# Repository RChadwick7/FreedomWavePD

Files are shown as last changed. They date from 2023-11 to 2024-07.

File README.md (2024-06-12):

# FreedomWavePD
### An open source version of the equipment used by researchers to treat Parkinson's Disease.
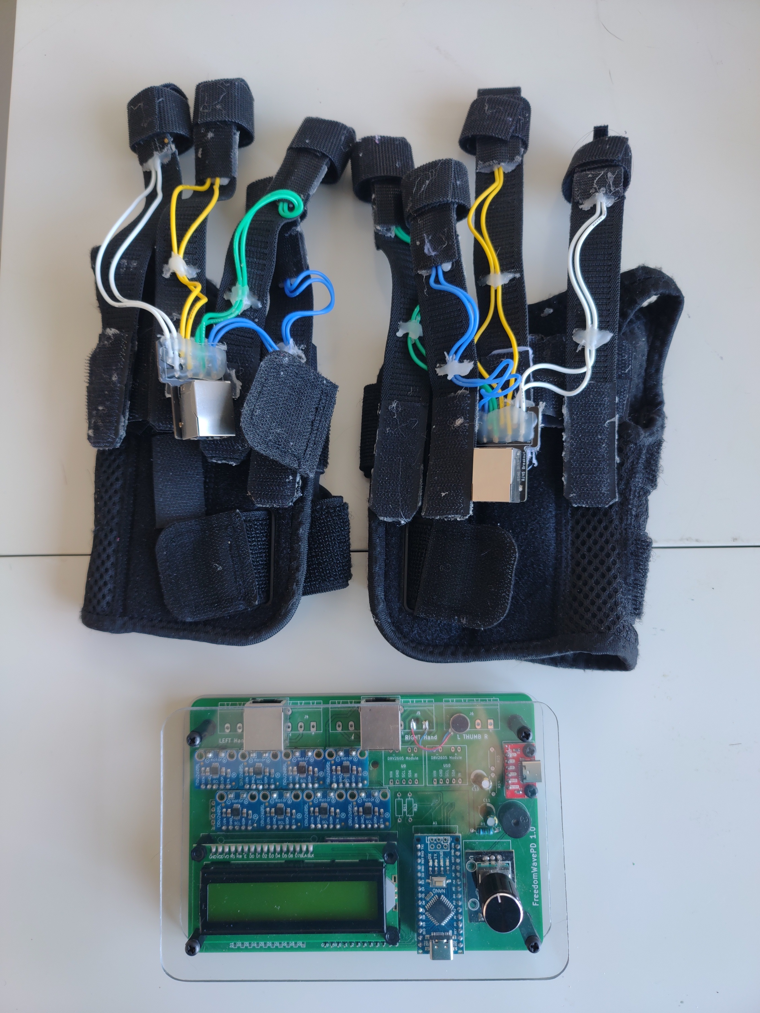
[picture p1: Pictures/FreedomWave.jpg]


- UPDATE 05-18-2024 The menu is now implemented in the firmware.
- UPDATE 02-19-2024 The PCB file should now be good. You can now see the assembly video here: https://youtu.be/leJTp28FIpU . The PCB used in the video had a few small mistakes that were corrected in the posted PCB and Gerbers, as well as the links to ordering a PCB.

**** If you don't know what this is, see this video: https://youtu.be/YEEwbxFT4Bc?feature=shared

Like many others, one morning I was watching the news and saw a story about Dr. Peter Tass at Stanford who was using vibrating gloves to treat Parkinson's Disease with amazing results. Realizing it might be years before they become available, I decided to make my own. What should have been a month of work stretched out to 8 months as I have very limited spare time. 

The theory of these gloves is relatively simple. You attach a device that either vibrates or physically pushes a small pin into the skin (NOT breaking the skin) to each finger, minus the thumbs (8 in total). These are activated in specific random patterns. The vibration triggers nerves in the fingers and these nerves go up to the brain. When these nerves are triggered in certain patterns, they can, in simple terms, help the brain straighten itself out. Look at Dr. Tass's work for much more detail.

The design goals were to make everything as flexible and adjustable as possible. While the results seem incredible, the researchers don't necessarily know the best settings yet. The gloves I constructed are bulky and awkward to put on but have the advantage of being able to put the vibrator anywhere on the fingertip. The circuit uses 8 DRV2605L haptic driver ic's but has room for 10 DRV2605L's in case there may be a benefit to using the thumbs. While these are more expensive than simple transistor drivers, they will easily drive both ERM and LRA vibrators. If there's demand, I'll design a daughterboard that will let this drive Piezo actuators.

Another design goal was to make this as easy as possible to make. I originally had hoped this could be done without soldering, but this just doesn't seem likely. My intention is that you will be able to order a PCB and all components, solder mostly modules to the PCB, and make the gloves. I have a video on YouTube showing step by step how to make the control box.

What are ERM and LRA motors? ERM stands for Eccentric Rotating Mass. Basically, they are motors that spin, and have an unbalanced weight on the output. When you add electricity, the motors spin, and they vibrate. LRA work a little differently. Linear Resonant Actuators have a magnet on a spring and a coil. If you have seen how loudspeakers work, these work on a very similar principle. When you add voltage, the coil generates a magnetic field and either repulses or attracts the magnet. If you reverse the polarity, the magnet is either attracted or repulsed, based on the polarity. If you keep alternating the polarity, the magnet will keep moving back and forth. While you can alternate the current at any frequency you want, these tend to resonate at specific frequencies and work best when you drive them at their resonant frequency.

The current state of the project is that everything should be functional. It implements all the patterns properly (I spent a LOT of time making sure randomness and jitter were spot on). The menu allows you to configure the control box to work with your specific gloves (ERM, LRA, Other) as well as treatment time, jitter, hand mirror, and others. More polish and features will be added as needed but everything is functional.

The project is divided into two parts: the gloves themselves, and the controller that runs and controls the gloves. While I don't currently have directions for making them, there are pictures here that should be enough to figure it out. You can also design your own gloves, or use some else's design. I will be mostly focusing on the controller, which is the harder and more critical part of the project. I'm currently looking into using audio transducers with a 3D Printed housing. Most files are already here but I will post more details as I get them.

The code is written in BASCOM BASIC, available at https://www.mcselec.com/ . It's not free but if you want to easily program microcontrollers it's worth every penny. I purchased a license over 20 years ago and I can't recommend it enough.

The schematic is in the Hardware folder. It looks complicated but it's mainly just wires. You could make this point-to-point but making a PCB is much easier. Be aware the schematic includes a lot of stuff you may not need. Two output connectors are added for the haptic actuators. You only need one. Also, I added driver IC's for thumbs. This isn't implemented. It's just there in case thumb actuators turn out to be useful in the future.

DISCLAIMER!!!!!!! I am NOT a Doctor. I don't make any claims that these gloves will do anything, including vibrate.

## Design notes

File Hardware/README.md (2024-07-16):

.<html><body>  <p>Can YOU make a FreedomWavePD? Odds are good but not everyone has the personality to complete this project. The most important qualities are a great deal of patience, the ability to work through frustration and an ability to follow directions precisely. It also doesn't hurt if you have some kind of mechanical aptitude. If you are unsure or need more confidence, I'd recommend picking one or two kits to assemble. A list is provided of recommended kits with the prices ranging from a few dollars up to around $12.</p><p><b>Quick list of steps:</b></p><ul><li>First thing you will need is a proper place to work. A table with newspaper or cardboard on it should be adequate. </li><li>Make sure your work area is well lit. </li><li>Make sure there are no distractions, animals, or children who might distract you. </li><li>Especially for the older of us, reading glasses or other magnification can be helpful. </li><li>Order all the needed parts, including the PCB. </li><li>Wait until they have all arrived. </li><li>Assembly should take 1-2 hours, or more. Take as long as you need. It's not a race. </li><li>After assembly, carefully check every solder connection. Look for connections where the solder has not properly flowed through both halves of the connection, as well as solder bridges where solder winds up where it's not supposed to be.</li><li>Program the Arduino chip.</li><li>Plug the Arduino chip in to the board.&nbsp;</li><li>Power up the board by plugging a USB-C cord into the power connector. </li><li>The display should show FreedomWavePD, followed by a revision number. The device does a self test. If there are any errors, take note. </li><li>Add the enclosure.</li></ul>
	<p>Done!</p><p><b>Ordering parts:</b> This project was made with a bit of versatility and flexibility in mind. When you build this board properly, you will see a lot of missing components on the Printed Circuit Board. THIS IS NORMAL. Not every slot was meant to be filled. Some parts are for future expansion, experimentation, or just in case there are issues with your particular parts. Follow the instructions and the video and you should end up with a working device.</p><p><b>Ordering a kit:</b> If you have never soldered or assembled an electronic kit before. I highly recommend you try a kit first. It will be good practice and give you confidence. There are a number of links to kits at Aliexpress.</p><p><b>Ordering the PCB:</b> The Printed Circuit Board, or PCB, will be ordered from a company that specializes in manufacturing PCB's. The process consists of sending then the FreedomWavePD Gerber files. While you can have any PCB company make your PCB, we have a link at JLCPCB.com to make ordering very easy. Simply click on this link:<a href="https://www.pcbway.com/project/shareproject/FreedomWavePD_1_1_5e7712c9.html">https://www.pcbway.com/project/shareproject/FreedomWavePD_1_1_5e7712c9.html</a>, fill in your address and payment info and everything else is all set for you. JLCPCB Requires purchasing 5 boards. As odd as this sounds, purchasing multiple boards is likely the cheapest way to get a single board. You can make more than one or share the extra boards with others.</p><p><b>Ordering the electronic components:</b> While there may be other sources, including Ebay, the two sources I decided on are Amazon and Aliexpress. Amazon will usually be much more expensive but you'll probably get the parts faster. Aliexpress has all the parts needed, at often a much lower price. Also, combining shipping or meeting certain minimums may result in shipping discounts. Unfortunately, a part with a similar description may not work with the FreedomWavePD. I have provided links to all parts. They have not all been tested but are believed to work. There are multiple links for each part in case one is not available or you want to order from Amazon instead of AliExpress. DO NOT ORDER FROM ALL LINKS or you will wind up with a lot of parts you don't need. For most parts, only one or two is needed. Sometimes, buying in higher quantities is actually cheaper than buying a single part. Others, parts are only available in minimum quantities. However, since you will need 8 driver modules it makes sense to shop around for the best price. The cheapest I have found was Aliexpress.</p><p><b>Ordering tools and consumables:</b> If you are already an electronics hobbyist, odds are VERY good you will not need any extra tools or supplies. Assuming you don't have the needed tools, links are provided for tools required to complete this project, as well as tools that likely will not be needed but could be helpful. </p>
	<p><b>Soldering Iron -</b> I STRONGLY recommend a soldering iron with an adjustable temperature. Keeping the temperature right is very important to adequate soldering. Aliexpress has them as low as $5.00 Soldering iron holder - You will be picking up and putting down the soldering iron a lot. It might be helpful to have a safe and convenient place to put or lay your soldering iron. 
	<p><b>Soldering iron tip cleaner -</b> The soldering iron can get crud on the tip and will need to be cleaned from time to time. Some soldering irons come with a dry, flat sponge. This is a tip cleaner. Get it wet. Wipe the hot tip over the damp sponge to clean the tip. Do it fast. There are also other tip cleaners that work without water. These work as well. If you're trying to do this cheap and don't have a tip cleaner, a wet paper towel can work. </p>
	<p><b>Solder -</b> There are two main varieties of solder - Lead-free and lead. Lead solder, actually a 60-40 mixture of lead and tin, has been used for decades and works very well. If you don't eat it or fail to wash your hands after use, it's perfectly safe and strongly recommended. Lead-free solder melts at a higher temperature and usually doesn't flow well, making it's use more difficult. Do NOT use solder meant for plumbing! This solder has an acid core and will make a mess for this purpose. </p>
	<p><b>Solder wick or desoldering pump -</b> These remove solder. Sometimes, you might find you have too much solder at a point. It might even bridge two or more points, which is very bad. You might also need to remove and replace a soldered part that is bad. In these cases, a way to remove solder is helpful. A solder pump literally sucks up the molten solder. Solder wick or braid will more gently and slowly pull the solder out of a solder conection. </p>
	<p><b>Flux -</b> Flux is literally a magic powder or cream that makes soldering work really well. Without flux, the solder can get chunky and sticky, connecting across multiple pins and causing problems. Solder actually comes with flux embedded in it's core. This is usually enough flux. You can purchase extra flux separately, and it may be useful. </p>
	<p><b>Alcohol -</b> Especially if you use extra flux, Alcohol is great for cleaning flux off a PCB. With the exception of the LCD and the speaker (Unless if the tab is still over the hole), all parts are safe to be sprayed, wiped, or even immersed in alcohol. Cleaning the board is probably not necessary but can make a neater finished product, as well as letting you examine connections for proper solder connections. </p>
	<p><b>Magnification -</b> This can be as simple as reading glasses, or more complicated with a magnifier with a built-in light. If you're young with good eyesight, you might not need any magnification at all. It's still good to have.</p>
	<p> <b>Files -</b> A file is not required, but very useful for smoothing edges and rounding corners, </p>
	<p><b>Multimeter -</b> While you won't need a multimeter to make a FreedomWavePD, you might need one if your project doesn't work after being finished. A multimeter can let you see what's going on in a way your eyes could never see. You can't tell if current is flowing or what the voltage is at a certain point just by looking. A multimeter lets you see what's going on.</p><dl><dt></dt></dl>
	<p><b>Kits</b></p><p><b>These kits are more difficult. If you can complete one of these, you can complete a FreedomWavePD</b></p><p><a href="https://www.aliexpress.us/item/3256805676517725.html">https://www.aliexpress.us/item/3256805676517725.html</a> Tetris Game $10.15</p>
	<p><a href="https://www.aliexpress.us/item/3256805975936653.html">https://www.aliexpress.us/item/3256805975936653.html</a> Spectrum Display $4.06 + $5.67&nbsp;</p>
	<p><a href="https://www.aliexpress.us/item/3256805694278758.html">https://www.aliexpress.us/item/3256805694278758.html</a> FM Radio kit $12.59&nbsp;</p>
	<p><a href="https://www.aliexpress.us/item/3256805979421046.html">https://www.aliexpress.us/item/3256805979421046.html</a> Clock $2.42 + $4.71&nbsp;</p>
	<p><a href="https://www.aliexpress.us/item/3256804493418967.html">https://www.aliexpress.us/item/3256804493418967.html</a>&nbsp;Hourglass $4.99</p>
	<dl><div>&nbsp; &nbsp; &nbsp; &nbsp; &nbsp;&nbsp;</div></dl><p><b>These kits are relatively easy. These are a good first try getting experience and confidence.</b></p><p><a href="https://www.aliexpress.us/item/3256805864804090.html">https://www.aliexpress.us/item/3256805864804090.html</a>&nbsp;Sound control LED $1.05 + $1.99&nbsp;</p>
	<p><a href="https://www.aliexpress.us/item/3256805864774178.html">https://www.aliexpress.us/item/3256805864774178.html</a>&nbsp;LED Top $1.02&nbsp;</p>
	<p><a href="https://www.aliexpress.us/item/3256805797252731.html">https://www.aliexpress.us/item/3256805797252731.html</a>&nbsp;Dice $1.49 + $1.99&nbsp;</p>
	<p><a href="https://www.amazon.com/Soldering-Practice-Electronics-Breathing-processing/dp/B0C1RKRXVP/ref=sr_1_2">https://www.amazon.com/Soldering-Practice-Electronics-Breathing-processing/dp/B0C1RKRXVP/ref=sr_1_2</a>&nbsp;$2.55&nbsp;</p>
	<p><a href="https://www.aliexpress.us/item/3256802950236508.html">https://www.aliexpress.us/item/3256802950236508.html</a>&nbsp;Light up bug kit $2.99&nbsp;</p>
	<p><a href="https://www.aliexpress.us/item/3256804393190704.html">https://www.aliexpress.us/item/3256804393190704.html</a>&nbsp;Flashlight $3.50</p>
	<p>&nbsp; &nbsp; &nbsp; &nbsp; &nbsp;&nbsp;</p><p><b>PARTS LIST</b> - These are the parts to complete the PCB of the main control unit. Parts for the gloves will be listed separately</p><p><b>PCB</b>&nbsp;<a href="https://www.pcbway.com/project/shareproject/FreedomWavePD_09ff3626.html">https://www.pcbway.com/project/shareproject/FreedomWavePD_09ff3626.html</a></p>
	<p>&nbsp; &nbsp; &nbsp; &nbsp; &nbsp;&nbsp;</p><p><b>DRV2605 Module (8 are needed)</b> </p>
	<p>$11.33&nbsp;<a href="https://www.amazon.com/Eujgoov-Controller-Management-Development-Vibration/dp/B097TTXGRN">https://www.amazon.com/Eujgoov-Controller-Management-Development-Vibration/dp/B097TTXGRN</a>&nbsp;</p>
	<p>$7.95&nbsp;<a href="https://www.mouser.com/ProductDetail/Adafruit/2305?qs=GURawfaeGuAbGO9ndi1lpg%3D%3D">https://www.mouser.com/ProductDetail/Adafruit/2305?qs=GURawfaeGuAbGO9ndi1lpg%3D%3D</a>&nbsp;</p>
	<p>$5.05, $43.46 for 8&nbsp;<a href="https://www.aliexpress.us/item/2255801044236410.html">https://www.aliexpress.us/item/2255801044236410.html</a>&nbsp;</p>
	<p>$4.50, $38.52 for 8 <a href="https://www.aliexpress.us/item/2255801054136853.html">https://www.aliexpress.us/item/2255801054136853.html</a></p>
	<p>&nbsp; &nbsp; &nbsp; &nbsp; &nbsp;&nbsp;</p><p><b>Arduino Nano v3 (Only 1 needed)</b> </p>
	<p>$2.00 + $1.75&nbsp;<a href="https://www.aliexpress.us/item/3256802779728607.html">https://www.aliexpress.us/item/3256802779728607.html</a>&nbsp;(Pick Color: Type-C) </p>
	<p>$11.99&nbsp;<a href="https://www.amazon.com/OSOYOO-ATmega328P-Module-Micro-Controller-Arduino/dp/B0BW3YLW1B/">https://www.amazon.com/OSOYOO-ATmega328P-Module-Micro-Controller-Arduino/dp/B0BW3YLW1B/</a></p>
	<p>&nbsp; &nbsp; &nbsp; &nbsp; &nbsp;&nbsp;</p><p><b>USB-C Board (Only 1 needed)</b></p>
	<p>$6.99 for 4&nbsp;<a href="https://www.amazon.com/Treedix-Type-C-Breakout-Connector-Converter/dp/B096M2HQLK/">https://www.amazon.com/Treedix-Type-C-Breakout-Connector-Converter/dp/B096M2HQLK/</a>&nbsp;</p>
	<p>$0.90 + $2.36 for 5&nbsp;<a href="https://www.aliexpress.us/item/3256804935738941.html">https://www.aliexpress.us/item/3256804935738941.html</a></p>
	<p>&nbsp; &nbsp; &nbsp; &nbsp; &nbsp;&nbsp;</p><p><b>1CJMCU-9548 (Only 1 needed)</b> </p>
	<p>$5.97 for 2&nbsp;<a href="https://www.amazon.com/Comimark-8-Channel-Muti-Channel-Expansion-Development/dp/B07V2FN3V3/">https://www.amazon.com/Comimark-8-Channel-Muti-Channel-Expansion-Development/dp/B07V2FN3V3/</a>&nbsp;</p>
	<p>$0.75 + $1.75 shipping&nbsp;<a href="https://www.aliexpress.us/item/3256805293304282.html">https://www.aliexpress.us/item/3256805293304282.html</a>&nbsp;</p>
	<p>$0.66 + $1.61 shipping&nbsp;<a href="https://www.aliexpress.us/item/3256805495885787.html">https://www.aliexpress.us/item/3256805495885787.html</a></p>
	<p>&nbsp; &nbsp; &nbsp; &nbsp; &nbsp;&nbsp;</p><p><b>Spacer Kit - Nylon (Only 1 needed)</b> </p>
	<p>$11.99&nbsp;<a href="https://www.amazon.com/gp/product/B09W563YG3/">https://www.amazon.com/gp/product/B09W563YG3/</a>&nbsp;</p>
	<p>$10.43&nbsp;<a href="https://www.aliexpress.us/item/3256803016697405.html">https://www.aliexpress.us/item/3256803016697405.html</a>&nbsp;(Pick Color: M3 650pcs)</p>
	<p>&nbsp; &nbsp; &nbsp; &nbsp; &nbsp;&nbsp;</p><p><b>Pack of headers and Sockets (Only 1 needed)</b> </p>
	<p>$1.96 + $1.72&nbsp;<a href="https://www.aliexpress.us/item/3256804851271117.html">https://www.aliexpress.us/item/3256804851271117.html</a>&nbsp;</p>
	<p>$2.50 + $0.53&nbsp;<a href="https://www.aliexpress.us/item/2251832538163556.html">https://www.aliexpress.us/item/2251832538163556.html</a>&nbsp;</p>
	<p>&nbsp; &nbsp; &nbsp; &nbsp; &nbsp;&nbsp;</p><p><b>Ethernet Connectors (2 are needed)</b> </p>
	<p>$0.85 + $2.69&nbsp;<a href="https://www.aliexpress.us/item/3256805919581391.html">https://www.aliexpress.us/item/3256805919581391.html</a>&nbsp;</p>
	<p>$1.73 + $1.96 for 10&nbsp;<a href="https://www.aliexpress.us/item/2251832663908888.html">https://www.aliexpress.us/item/2251832663908888.html</a>&nbsp;</p>
	<p>$8.89 for 10&nbsp;<a href="https://www.amazon.com/FMHXG-Shielded-Network-Connector-Computer/dp/B0BRQ2R8HW">https://www.amazon.com/FMHXG-Shielded-Network-Connector-Computer/dp/B0BRQ2R8HW</a>&nbsp;</p>
	<p>&nbsp; &nbsp; &nbsp; &nbsp; &nbsp;&nbsp;</p><p><b>Capacitors 100uF (2 are needed)&nbsp;</b></p>
	<p>$1.08 + $1.59&nbsp;<a href="https://www.aliexpress.us/item/2251832863141576.html">https://www.aliexpress.us/item/2251832863141576.html</a>&nbsp;50 PCS. Select 16V100UF 50PCD </p>
	<p>$2.42 + $2.91&nbsp;<a href="https://www.aliexpress.us/item/3256802907683211.html">https://www.aliexpress.us/item/3256802907683211.html</a>&nbsp;10 PCS. Select 16V100UF 5X11 </p>
	<p>$1.36 + $1.75 for 10&nbsp;<a href="https://www.aliexpress.us/item/3256802111565574.html">https://www.aliexpress.us/item/3256802111565574.html</a>&nbsp;10 PCS. Select 16V100UF 10PCS</p>
	<p>&nbsp; &nbsp; &nbsp; &nbsp; &nbsp; &nbsp;</p><p><b>Rotary Encoder (Only 1 is needed)</b> </p>
	<p>$0.43 + $0.75&nbsp;<a href="https://www.aliexpress.us/item/3256801435584649.html">https://www.aliexpress.us/item/3256801435584649.html</a>&nbsp;For ONE No knob </p>
	<p>$3.10 + $1.71&nbsp;<a href="https://www.aliexpress.us/item/3256804834159169.html">https://www.aliexpress.us/item/3256804834159169.html</a>&nbsp;For FIVE Select Color 5pcs KY-040 Cap</p>
	<p>&nbsp; &nbsp; &nbsp; &nbsp; &nbsp; &nbsp;</p><p><b>Speaker (Only 1 is needed)</b> </p>
	<p>$0.46 + $1.75&nbsp;<a href="https://www.aliexpress.us/item/2251832159763853.html">https://www.aliexpress.us/item/2251832159763853.html</a>&nbsp;FOR 10 Select Color: Passive Buzzer 16R </p>
	<p>$7.28&nbsp;<a href="https://www.amazon.com/Gikfun-Terminals-Passive-Electronic-Arduino/dp/B01GJLE5BS">https://www.amazon.com/Gikfun-Terminals-Passive-Electronic-Arduino/dp/B01GJLE5BS</a>&nbsp;FOR 10</p>
	<p>&nbsp; &nbsp; &nbsp; &nbsp; &nbsp; &nbsp;</p><p><b>120 Ohm resistor (Only 1 is needed)</b> </p>
	<p>$5.39 for 10&nbsp;<a href="https://www.amazon.com/Projects-10EP512120R-120-Resistors-Pack/dp/B07JHT7ZJL/">https://www.amazon.com/Projects-10EP512120R-120-Resistors-Pack/dp/B07JHT7ZJL/</a>&nbsp;</p>
	<p>$2.22 for 100&nbsp;<a href="https://www.aliexpress.us/item/2251832874311613.html">https://www.aliexpress.us/item/2251832874311613.html</a>&nbsp;Pick Resistance:120R </p>
	<p>$3.72 for 300 assortment&nbsp;<a href="https://www.aliexpress.us/item/3256804977975040.html">https://www.aliexpress.us/item/3256804977975040.html</a>&nbsp;Pick Resistance: 300PCS KIT BOX</p>
	<p>&nbsp; &nbsp; &nbsp; &nbsp; &nbsp; &nbsp;</p><p><b>16x2 LCD I2C (Only 1 is needed)</b> </p>
	<p>$1.56 + $1.86&nbsp;<a href="https://www.aliexpress.us/item/3256802537284239.html">https://www.aliexpress.us/item/3256802537284239.html</a>&nbsp;(Pick Color:IIC LCD1602C Bule or IIC LCD1602C Green) (Yes, I meant Bule)&nbsp;</p>
	<p>$10.99 for 2&nbsp;<a href="https://www.amazon.com/GeeekPi-Character-Backlight-Raspberry-Electrical/dp/B0BCWFB5P3/">https://www.amazon.com/GeeekPi-Character-Backlight-Raspberry-Electrical/dp/B0BCWFB5P3/</a>&nbsp;FOR 2 - Green </p>
	<p>$10.99 for 3&nbsp;<a href="https://www.amazon.com/Hosyond-Display-Module-Arduino-Raspberry/dp/B0BWTFN9WF?th=1">https://www.amazon.com/Hosyond-Display-Module-Arduino-Raspberry/dp/B0BWTFN9WF?th=1</a> For 3</p>
	<p>&nbsp; &nbsp; &nbsp; &nbsp; &nbsp; &nbsp;</p><p><b>4 x 6 Plexiglas (2 4x6 pieces are required. Larger pieces can be cut)</b> </p>
	<p>$5.99 Select 4x6,1mm thick, 6 pieces&nbsp;<a href="https://www.amazon.com/Langaelex-Thickness-Extruded-Plexiglass-Replacement/dp/B09KXZ2HPD">https://www.amazon.com/Langaelex-Thickness-Extruded-Plexiglass-Replacement/dp/B09KXZ2HPD</a>&nbsp;</p>
	<p>$1.99 for one&nbsp;<a href="https://www.michaels.com/product/clear-acrylic-craft-sheet-by-make-market-10689055">https://www.michaels.com/product/clear-acrylic-craft-sheet-by-make-market-10689055</a>&nbsp;</p>
	<p>$11.98 for 6&nbsp;<a href="https://www.amazon.com/Lesnlok-Acrylic-Plexiglass-Display-Projects/dp/B0C3V29F4H?th=1">https://www.amazon.com/Lesnlok-Acrylic-Plexiglass-Display-Projects/dp/B0C3V29F4H?th=1</a>&nbsp;Select 4 x 6 </p>
	<p>$7.99 for enough to make at least 2&nbsp;<a href="https://www.amazon.com/Polycarbonate-Resistant-Plexiglass-Robotics-Industrial/dp/B07VVGL6GV">https://www.amazon.com/Polycarbonate-Resistant-Plexiglass-Robotics-Industrial/dp/B07VVGL6GV</a></p>
	<p>&nbsp; &nbsp; &nbsp; &nbsp; &nbsp; &nbsp; &nbsp; &nbsp; &nbsp; &nbsp;&nbsp;</p>
	<p><b>Tools</b></p><p>If you don't have tools, here is a list of options:</p><p><b>Soldering iron</b></p>
	<p><a href="https://www.aliexpress.us/item/3256805582397020.html">https://www.aliexpress.us/item/3256805582397020.html</a>&nbsp;$6.35 US or EU plug&nbsp;</p>
	<p><a href="https://www.aliexpress.us/item/3256805437517395.html">https://www.aliexpress.us/item/3256805437517395.html</a>&nbsp;$4.53 soldering only, $7.13 for stand, sucker, solder</p>
	<p><a href="https://www.aliexpress.us/item/3256804005154298.html">https://www.aliexpress.us/item/3256804005154298.html</a>&nbsp;$9.21 Iron, flux, solder, stand</p>
	<p>&nbsp; &nbsp; &nbsp; &nbsp; &nbsp;&nbsp;</p><p><b>flux</b></p>
	<p><a href="https://www.aliexpress.us/item/3256805912053547.html">https://www.aliexpress.us/item/3256805912053547.html</a> $3.21</p>
	<p><a href="https://www.aliexpress.us/item/2255800964358053.html">https://www.aliexpress.us/item/2255800964358053.html</a> $0.99 + $2.79</p>
	<p> &nbsp; &nbsp; &nbsp; &nbsp; &nbsp;</p><p><b>3mm drill&nbsp;</b></p>
	<p><a href="https://www.aliexpress.us/item/3256805878623159.html">https://www.aliexpress.us/item/3256805878623159.html</a>&nbsp;$1.76 Drill holder and drills</p>
	<p>&nbsp; &nbsp; &nbsp; &nbsp; &nbsp;&nbsp;</p><p><b>Acid brushes (Flux Brushes)&nbsp;</b></p>
	<p><a href="https://www.aliexpress.us/item/3256805343437473.html">https://www.aliexpress.us/item/3256805343437473.html</a>&nbsp;$0.21 + $1.91&nbsp;</p>
	<p><a href="https://www.harborfreight.com/12-in-horsehair-bristle-acid-shop-brushes-36-piece-61880.html">https://www.harborfreight.com/12-in-horsehair-bristle-acid-shop-brushes-36-piece-61880.html</a>&nbsp;$2.99</p>
	<p>&nbsp; &nbsp; &nbsp; &nbsp; &nbsp;&nbsp;</p><p><b>Alcohol&nbsp;</b></p>
	<p><a href="https://www.walmart.com/ip/Equate-91-Isopropyl-Alcohol-Antiseptic-16-fl-oz/746603118">https://www.walmart.com/ip/Equate-91-Isopropyl-Alcohol-Antiseptic-16-fl-oz/746603118</a>&nbsp;$2.76</p>
	<p>&nbsp; &nbsp; &nbsp; &nbsp; &nbsp;&nbsp;</p><p><b>CHEAP Multimeter&nbsp;</b></p>
	<p><a href="https://www.aliexpress.us/item/3256805814945255.html">https://www.aliexpress.us/item/3256805814945255.html</a>&nbsp;- $2.82 + $5.66&nbsp;</p>
	<p><a href="https://www.aliexpress.us/item/3256803879810074.html">https://www.aliexpress.us/item/3256803879810074.html</a>&nbsp;- $2.89 + $5.64&nbsp;</p>
	<p><a href="https://www.aliexpress.us/item/3256804632557862.html">https://www.aliexpress.us/item/3256804632557862.html</a>&nbsp;- $2.98 + $6.54&nbsp;</p>
	<p><a href="https://www.harborfreight.com/electrical/electrician-s-tools/multimeters-testers/7-function-digital-multimeter-59434.html">https://www.harborfreight.com/electrical/electrician-s-tools/multimeters-testers/7-function-digital-multimeter-59434.html</a>&nbsp;$6.99</p>
	<p>&nbsp; &nbsp; &nbsp; &nbsp; &nbsp;&nbsp;</p><p><b>Magnification</b>&nbsp;</p>
	<p><a href="https://www.harborfreight.com/head-lamp-magnifier-58788.html">https://www.harborfreight.com/head-lamp-magnifier-58788.html</a>&nbsp;$13.99</p>
	</body></html>

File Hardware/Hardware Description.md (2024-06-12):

# Hardware Description

The microcontroller for this is an Arduino Nano v3.0. The output pins go to a TCA9548A, which allows programming the DRV2605L driver IC's individually (Since the driver chips all have the same address). The I2C bus also goes to the LCD. 8 or 10 lines from PortD go to each DRV2605L to allow triggering without the overhead of using I2C. The PCB also has room for LED's and a connector so these outputs can be observed. The outputs of the DRV2605L's go directly to the ERM/LRA vibrators. The DRV2605L can work with a 4 Ohm load.

There are pads at each driver module for a surface mount capacitor across the power input. A capacitor may be needed here, depending on your application.

There are pads at each driver module for a surface mount TVS diode. If you are driving a high inductance load, such as actuators made with relays, you might want a TVS diode to protect the driver modules from back EMF.

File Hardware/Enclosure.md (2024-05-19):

# Assembling the enclosure
While you are welcome to put the PCB in any enclosure you want, the PCB was designed to be sandwiched between two pieces of Lexan. The Lexan sheets usually come with protective plastic on both sides. It's recommended you leave this on until you're done drilling and filing. Instructions:

1) Cut two pieces of Lexan (Polycarbonate) exactly 4 inches x 6 inches.
2) Drill 3mm holes near each corner. The holes are placed exactly 1/2 inch from the edge. If you have access to a 3D printer, you can print the corner_jig which will give you a guide as to where to drill. Or, if you have an extra PCB you can use it as a template. Using thin, Scotch tape-like double sided tape, attach the PCB to the Lexan sheet. Drill the 4 corner holes. Do this with both sheets. One sheet will be the front, the other the back.
3) On one of the sheets, drill a single hole 3/4 inch from the side, 1 1/4 inch from the bottom. You can also use the PCB as a template. There are three holes on the rectangular rotary encoder (control knob). Drill the hole in the center. This hole is for the knob. This sheet will be the top
4) While it's not required, it will make a neater and safer enclosure to round the corners. These can be rounded using a file. The corner jig can be used to get the radius consistent. You can also use a PCB as a template.
5) It's recommended you put a spacer in the hole in the middle of the PCB. This will add rigidity. Also, a spacer should be placed in the center hole under the rotary encoder. This will give support when the encoder is pushed.
6) Using spacers, screws, nuts from the 3mm Nylon screw kit, install spacers in the corners that are slightly taller than the LCD. If you get this height right, you can install the rotary encoder on the front Lexan sheet and it will neatly plug into the socket installed on the PCB. Depending on the Nylon screw kit you got, it might take some experimenting to find the best height. Be aware the lower left hole shares the hole with the LCD module so you will need a shorter spacer. With all 4 corners the same height, place the lexan sheet and screw 4 nylon screws in the corners. For the bottom, use shorter spacers.

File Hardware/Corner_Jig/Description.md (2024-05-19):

# Corner Jig
This tool is not required, but handy if you have a 3D printer.

Assuming you are using a plastic sheet exactly 4 inches by 6 inches. this will locate the mounting holes. Simply slip on each corner snugly and drill in the hole. 

This can also be used as a template to file a nice rounded corner.

Once drilling the holes, using a 3mm drill, the resulting 4x6 plastic sheet can be used as either a top or bottom covering for the printed circuit board.

Plexiglas is not recommended as it cracks very easily.

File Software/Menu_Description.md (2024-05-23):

<html><body> <h2><br/><strong>This is the menu layout:</strong></h2><p><strong>Start Therapy</strong><br/><strong>Stop Therapy</strong><br/><strong>Device Settings</strong><br/>&nbsp;&nbsp;&nbsp;&nbsp;- Autostart<br/>&nbsp;&nbsp;&nbsp;&nbsp;- Load Defaults<br/>&nbsp;&nbsp;&nbsp;&nbsp;- <i>Back</i><br/><strong>Therapy Settings</strong><br/>&nbsp; &nbsp;- SessionMinutes<br/>&nbsp;&nbsp;&nbsp;&nbsp;- Intensity<br/>&nbsp;&nbsp;&nbsp;&nbsp;- Jitter<br/>&nbsp;&nbsp;&nbsp;&nbsp;- Hand Mirror<br/>&nbsp;&nbsp;&nbsp;&nbsp;- <i>Back</i><br/><strong>Advanced</strong><br/>&nbsp; &nbsp;- Drive Voltage<br/>&nbsp;&nbsp;&nbsp;&nbsp;- LRA Frequency<br/>&nbsp;&nbsp;&nbsp;&nbsp;- ERM/LRA Status<br/>&nbsp;&nbsp;&nbsp;&nbsp;- Set LRA<br/>&nbsp;&nbsp;&nbsp;&nbsp;- OL/CL Status<br/>&nbsp;&nbsp;&nbsp;&nbsp;- Set Open Loop<br/>&nbsp;&nbsp;&nbsp;&nbsp;- <i>Back</i><br/><strong>About</strong></p><p>&nbsp;</p><h2><br/><strong>Description:</strong></h2><p><strong>Start Therapy:</strong> Starts therapy. Therapy will run for the length of minutes set in SessionMinutes, then stop.</p><p><strong>Stop Therapy:</strong> This will stop Therapy early</p><p><strong>Autostart:</strong> This configures whether or not therapy starts as soon as the device is powered on. This does the same thing as the solder jumper on the PCB</p><p><strong>Load Defaults:</strong> This loads settings to a known state if you get lost and change too much. While this loads variables in, they are not saved permanently. To save a setting permanently, load defaults and then go to the setting you want to save. Select it, then save it by pushing the rotary knob twice.</p><p><strong>SessionMinutes:</strong> This is how many minutes each session will last.</p><p><strong>Intensity:</strong> This adjust how intense the vibrations are.</p><p><strong>Jitter:</strong> This adjusts how much random jitter is injected into the finger patterns.</p><p><strong>Hand Mirror:</strong> Only 4 random fingers are selected each cycle, and are copied to the other hand. For instance, both index fingers may get activated, then both pinkies, then both ring fingers, then both middle fingers. If Hand Mirror is enabled, an Index finger on one hand and the pinky finger of the other hand will activate at the same time, the middle finger on one hand and the ring finger of the other will activate at the same time, etc. It's the same as taking the actuators off one hand and putting them back in reverse order.</p><p><strong>Drive Voltage:</strong> This is the drive voltage of the actuators. Going above rated voltages can damage the actuators. For ERM and LRA vibrators, this should be specified in the datasheet or accompanying literature, and is likely around 1.5V. For DAEX type audio exciters, this can likely be set higher.</p><p><strong>LRA Frequency:</strong> In Open loop mode, this will set the driver IC to vibrate the actuator at this frequency. The original gloves used 250Hz so that is a safe setting.</p><p><strong>ERM/LRA Status:</strong> This shows what the current setting is, either ERM, or LRA.</p><p><strong>Set LRA:</strong> If this is set ON, then the device is configured to work with LRA vibrators. If it is set to OFF, it is configured to work with ERM vibrators.</p><p><strong>OL/CL Status:</strong> This shows wheter the system is currently set to Open or Closed loop configuration. Closed loop tries to resonate the vibrator at it's resonant frequency. If you are using an off the shelf LRA, it may be best to set this to Closed loop. Audio Actuators don't have a specified resonant frequency and Closed loop mode may have a hard time locking in. With these actuators, Open loop is preferred.</p><p><strong>Set Open Loop:</strong> If this is set to ON, then the device is configured to run LRA vibrators in Open loop mode. If this is set to OFF, it is configured to run LRA vibrators in Closed loop mode.<br/>&nbsp;</p>
</body></html>

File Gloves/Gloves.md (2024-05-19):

# Glove Options
There are basically two different types of actuators available. One simply vibrates. This is fairly easy to do, using either ERM or LRA vibrators. However, this is not what Dr. Peter Tass uses. The gloves used by Dr. Tass are tactors that physically push into the skin rapidly. This might seem the same but the theory is that the right nerves are stimulated by tactors. The gloves I created simply vibrate. Although I did observe positive results, my effort is now going into tactors. There are basically two categores of tactors. One is Magnetic, the other Piezo. While the FreedomWavePD should be able to drive the magnetic tactors, I will need to develop a daughterboard to mount on the FreedomWavePD to work with the Piezo tactors, if that need arises. Piezo tactors appear very expensive so most of the effort has cenered around magnetic tactors.

The first version of FreedomWavePD gloves are not described, but there are a lot of pictures, including pictures with measurements. These work and are easy to make, but are not ideal, as described above.

Another option is the V2 of FreedomWavePD gloves. I haven't made these yet. They are similar to V1 but have a hole the size of the LRA motor. The motor would be free to move within the hole. Either spandex or elastic goes on the outside covering the hole. The LRA motor is attached to the spandex/elastic. This isolates the vibration from the Velcro.

There are a number of gloves and actuators developed by varios people. Here are the ones I've found:

Dayton DAEX 13 mounting kit - This is a 3D printed housing for the Dayton DAEX-13-4SM actuator. You'll have to be creative attaching them to the fingertips. You also may need to put a 4 Ohm 3W resistor in series to let the FreedomWavePD controller run these safely. https://www.thingiverse.com/thing:6138476

Godef v2.3 Latest, has stylus on tips. Not released yet.

Godef v2.2 - 3D printed clip-on housing for the Tectonic TEAX09C005-8 actuator, which unfortunately is currently sold out from most resellers. This should work directly with the FreedomWavePD Control unit, configured to use LRA. Located here: https://bb.f2heal.com/viewtopic.php?t=47 and here: https://github.com/F2HEAL/VHP-Vibro-Glove2/

Godef 2.0 - These use the same Tectonic TEAX09C005-8 actuator but do not have the clip to hold them on to the fingertip. Located here: https://bb.f2heal.com/viewtopic.php?t=9

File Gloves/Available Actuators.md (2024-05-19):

### Dayton DAEX-13-4SM - Used by Winnie The Poo. Available on Amazon $10, Parts Express $5
- 4 Ohm
- 13mm voice coil
- p-p Excursion not listed
- 0.75 x 1.5 x 0.3 inches

### Dayton DAEX-9-4SM - Nobody is using,. Available on Parts Express $4
- 4 Ohm
- 9mm voice coil
- p-p Excursion not listed
- 0.5 x 1 x 0.25 inches - Almost the same size as the elusive TEAX09C005-8. Fits GODEF if you cut the tabs off

### Tectonic TEAX09C005-8 - Used by GODEF F2Heal - Impossible to buy in the US.
- 8 Ohm
- 8.7mm voice coil
- 1.2mm P-P Excursion
- 13 x 26 x 6.5mm (0.51 x 1.02 x 0.25 Inches)

### Tectonic TEAX14C02-8 - Available from Parts Express $4
- 8 Ohm
- 14mm voice coil
- p-p Excursion not listed
- 20 x 37 x 9.85mm (0.79 x 1.46 x 0.39 Inches) May be a good 8 ohm replacement for the DAEX-13-4SM.

---------------------------------------
Other options -

### DAEX9CT-4 - Nobody is using, looks like a good choice
- 4 Ohms
- 9mm voice coil
- p-p Excursion not listed
- 20.9mm x 8.5mm

Also, another brand is billionsound. Available on Alibaba - https://www.alibaba.com/product-detail/9mm-1W-4-Ohm-Skinny-Mini_60520851923.html

### Billionsound 14J16 (RMD000914J16-BS)
- 4 Ohms
- 9mm voice coil
- 11 x 24 x 5 mm

### HiWave HIHX9C005-8 Also HIAX9C005-8 - Looks a LOT like Tectonic...
- 8 Ohms (Also available in 4, 16, 32)
- 9mm voice coil
- 12 x 26 x 6mm

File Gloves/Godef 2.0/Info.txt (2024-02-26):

Full info is located here: https://bb.f2heal.com/viewtopic.php?p=11

3D design housing and contactor pin for TECTONIC TEAX09C005-8 Audio Exciters | design pgodefroy

We have chosen a tight press fit of the TEAX9, instead of glueing them against a fix stop. This should allow us to play with the length of how much the contactor protrudes from the housing and also to compensate for tolerances.

The dimension of the housing are 31x18x17 mm (lxwxh).
The diameter of the contactor pin is 4 mm.

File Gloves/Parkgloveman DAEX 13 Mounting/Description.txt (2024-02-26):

Dayton Exciter

From WinnieThePoo:
Ok. The product code is DAEX-13-4SM. They are 8 euros from sound imports in Italy, which is where I buy them. I'm sure you'll find them in the USA easily enough. 

https://www.thingiverse.com/thing:6138476

They are secured with M3 6mm steel bolts which self-tap into the soft plastic PLA.  They are not symmetrical.  Once you use the guide rod to fix the plastic disc to the adhesive on the exciter, then they have to fit in the housing that way round.  If you put them in reversed, the contact pin will be a bit off-centre.

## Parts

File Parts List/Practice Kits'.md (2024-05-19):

   ##   Electronic kits ranked roughly from difficult to easy
	  
### These kits are more difficult. If you can complete one of these, you can complette a FreedomWavePD	  
- https://www.aliexpress.us/item/3256805676517725.html Tetris Game $10.15
- https://www.aliexpress.us/item/3256805975936653.html Spectrum Display $4.06 + $5.67
- https://www.aliexpress.us/item/3256805694278758.html FM Radio kit $12.59
- https://www.aliexpress.us/item/3256805979421046.html Clock $2.42 + $4.71
- https://www.aliexpress.us/item/3256804493418967.html Hourglass $4.99

### These kits are relatively easy. These are a good first try getting experience and confidence.

- https://www.aliexpress.us/item/3256805864804090.html Sound control LED $1.05 + $1.99
- https://www.aliexpress.us/item/3256805864774178.html LED Top $1.02
- https://www.aliexpress.us/item/3256805797252731.html Dice $1.49 + $1.99
- https://www.amazon.com/Soldering-Practice-Electronics-Breathing-processing/dp/B0C1RKRXVP/ref=sr_1_2 $2.55
- https://www.aliexpress.us/item/3256802950236508.html Light up bug  kit $2.99
- https://www.aliexpress.us/item/3256804393190704.html Flashlight $3.50

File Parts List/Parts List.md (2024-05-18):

# Control Unit:

### DRV2605 Module (8 Needed)

 - $11.33 https://www.amazon.com/Eujgoov-Controller-Management-Development-Vibration/dp/B097TTXGRN
 - $7.95 https://www.mouser.com/ProductDetail/Adafruit/2305?qs=GURawfaeGuAbGO9ndi1lpg%3D%3D
 - $5.05, $43.46 for 8 https://www.aliexpress.us/item/2255801044236410.html
 - $4.50 $38.52 for 8 https://www.aliexpress.us/item/2255801054136853.html

### Arduino Nano v3 (One needed)

 - $2.00 + $1.75  https://www.aliexpress.us/item/3256802779728607.html (Pick Color: Type-C)
 - $11.99  https://www.amazon.com/OSOYOO-ATmega328P-Module-Micro-Controller-Arduino/dp/B0BW3YLW1B/

### USB-C Board (One Needed) - Be aware the Adafruit board looks almost the same, but the pins are wired differently. If you substitute this make SURE the pins are correct.

 - $6.99 for 4 https://www.amazon.com/Treedix-Type-C-Breakout-Connector-Converter/dp/B096M2HQLK/
 - $0.90 + $2.36 for 5 https://www.aliexpress.us/item/3256804935738941.html  

### CJMCU-9548 (One Needed)

- $5.97 for 2 https://www.amazon.com/Comimark-8-Channel-Muti-Channel-Expansion-Development/dp/B07V2FN3V3/
- $0.75 + $1.75 shipping https://www.aliexpress.us/item/3256805293304282.html
- $0.66 + $1.61 shipping https://www.aliexpress.us/item/3256805495885787.html

### Spacer Kit - Nylon (One Needed)

  - $11.99 https://www.amazon.com/gp/product/B09W563YG3/
  - $10.43 https://www.aliexpress.us/item/3256803016697405.html (Pick Color: M3 650pcs)

### Pack of headers AND Sockets (One Needed)

- $1.96 + $1.72 https://www.aliexpress.us/item/3256804851271117.html
- $2.50 + $0.53 https://www.aliexpress.us/item/2251832538163556.html  HAS SOCKETS TOO!

### Ethernet Connectors (Two Needed)

 - $0.85 + $2.69 https://www.aliexpress.us/item/3256805919581391.html
 - $1.73 + $1.96 https://www.aliexpress.us/item/2251832663908888.html
 - $8.89 for 10 https://www.amazon.com/FMHXG-Shielded-Network-Connector-Computer/dp/B0BRQ2R8HW

### Capacitors 100uF (Two Needed)

 - $1.08 + $1.59 https://www.aliexpress.us/item/2251832863141576.html  50 PCS. Select 16V100UF 50PCD
 - $2.42 + $2.91 https://www.aliexpress.us/item/3256802907683211.html 10 PCS. Select 16V100UF 5X11

### Rotary Encoder (One Needed) - Be aware that, if you get these from a different source, some come without a nut or threads.

  - $2.47 https://www.aliexpress.us/item/3256805609786051.html For ONE
  - $0.43 + $0.75 https://www.aliexpress.us/item/3256801435584649.html For ONE

 ### Speaker )One Needed)

 - $0.46 + $1.75 https://www.aliexpress.us/item/2251832159763853.html  FOR 10  Select Color: Passive Buzzer 16R
 - $7.28 https://www.amazon.com/Gikfun-Terminals-Passive-Electronic-Arduino/dp/B01GJLE5BS  FOR 10

### 120 Ohm resistor (One Needed)

  - $5.39 for 10 https://www.amazon.com/Projects-10EP512120R-120-Resistors-Pack/dp/B07JHT7ZJL/
  - $2.22 for 100 https://www.aliexpress.us/item/2251832874311613.html  Pick Resistance:120R
  - $3.72 for 300 assortment https://www.aliexpress.us/item/3256804977975040.html Pick Resistance: 300PCS KIT BOX

### 16x2 LCD I2C (One Needed)

  - $10.99 for 2 https://www.amazon.com/GeeekPi-Character-Backlight-Raspberry-Electrical/dp/B0BCWFB5P3/ FOR 2 - Green - Known to fit well
  - $10.99 for 3 https://www.amazon.com/Hosyond-Display-Module-Arduino-Raspberry/dp/B0BWTFN9WF?th=1 FOR 3 - Should fit.
  - $1.56 + $1.86 - These are the cheapest but WILL NOT FIT PROPERLY. They will need the leads to be bent to fit. The Contrast control won't line up with the hole. Electrically they should work fine. https://www.aliexpress.us/item/3256802537284239.html (Pick Color:IIC LCD1602C Bule or IIC LCD1602C Green)

### 4 x 6 Polycarbonate (One Needeed)

 It is strongly recommended you use Lexan/Polycarbonate. Acrylic(Plexiglas) cracks very easily

 - $7.99 for enough to make at least 2 https://www.amazon.com/Polycarbonate-Resistant-Plexiglass-Robotics-Industrial/dp/B07VVGL6GV

### PCB (One Needed)

  - $55.00 for 5 boards https://www.pcbway.com/project/shareproject/FreedomWavePD_1_1_5e7712c9.html

  - $120 for 3 boards https://oshpark.com/shared_projects/di3AwB5o

# Gloves:

### Velcro

### LRA Vibrators

- $11.50 for 8 including shipping https://www.lcsc.com/product-detail/Vibration-Motor_LEADER-LD0832AA-0099F_C2682305.html   

### Ethernet Breakout

  - $1.58 + $2.39 https://www.aliexpress.us/item/3256805828204648.html   FOR ONE
  - $1.20 + $2.08 https://www.aliexpress.us/item/3256805190110568.html
  - $2.74 for one https://www.aliexpress.us/item/3256804925465135.html Select Colorl: 4
  - $8.99 https://www.amazon.com/Treedix-Connector-Breakout-Replacement-Unassembled/dp/B08RYFJ7ZG  INCLUDES 2

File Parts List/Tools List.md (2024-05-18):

### Soldering iron
- https://www.aliexpress.us/item/3256805582397020.html $6.35 US or EU plug
- https://www.aliexpress.us/item/3256805437517395.html $4.53 soldering only, $7.13 for stand, sucker, solder
- https://www.aliexpress.us/item/3256804005154298.html $9.21 Iron, flux, solder, stand

### Soldering iron kit (Iron, solder, flux, iron holder)
- https://www.amazon.com/Soldering-soldering-solder-adjustable-temperature/dp/B09DY7CCW5?th=1 - $10

### Solder
- https://www.amazon.com/Solder-Diameter-Storage-Welding-Soldering/dp/B01N0VNNKO/?th=1 - $5.00

### Flux
- https://www.amazon.com/PD-10-Solid-Welding-Soldering-Solder/dp/B00KCJAHFM - $5.00

### Cheap manual drill with 3mm drill
- https://www.amazon.com/gp/product/B08T6Y3PL5 - $7.00

### Acid brushes
- https://www.harborfreight.com/12-in-horsehair-bristle-acid-shop-brushes-36-piece-61880.html - $3.00

### Alcohol
- https://www.walmart.com/ip/Equate-91-Isopropyl-Alcohol-Antiseptic-16-fl-oz/746603118 - $2.75

### CHEAP Multimeter
- https://www.aliexpress.us/item/3256805814945255.html - $2.82 + $5.66
- https://www.aliexpress.us/item/3256803879810074.html - $2.89 + $5.64
- https://www.aliexpress.us/item/3256804632557862.html - $2.98 + $6.54
- https://www.amazon.com/QLUUE-Multimeter-Resistance-Continuity-Automotive/dp/B09Q3134VW - $8.00

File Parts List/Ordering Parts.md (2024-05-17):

<html><body> <p><b>Ordering parts:</b> This project was made with a bit of versatility and flexibility in mind. When you build this board properly, you will see a lot of missing components on the Printed Circuit Board. THIS IS NORMAL. Some parts are for future expansion, experimentation, or just in case there are issues with your particular parts. Follow the instructions and the video and you should end up with a working device.</p><p><b>Ordering a kit:</b> If you have never soldered or assembled an electronic kit before. I highly recommend you try a kit first. It will be good practice and give you confidence. There are a number of links to kits at Aliexpress.</p><p><b>Ordering the PCB:</b> The Printed Circuit Board, or PCB, will be ordered from a company that specializes in manufacturing PCB's. The process requires sending them the FreedomWavePD Gerber files. While you can have any PCB company make your PCB, we have a link at JLCPCB.com and OSHPark.com to make ordering very easy. Simply click on the link, fill in your address and payment info and everything else is all set for you. JLCPCB Requires purchasing 5 boards. As odd as this sounds, purchasing 5 boards from JLCPCB is likely the cheapest way to get a single board. You can make more than one or share the extra boards with others.</p><p><b>Ordering the electronic components:</b> While there may be other sources, including Ebay, the two sources I decided on are Amazon and Aliexpress. Amazon will usually be much more expensive but you'll probably get the parts faster. Aliexpress has all the parts needed, at often a much lower price. Also, combining shipping or meeting certain minimums may result in shipping discounts. Unfortunately, a part with a similar description may not work with the FreedomWavePD. I have provided links to all parts. They have not all been tested but are believed to work. There are multiple links for each part in case one is not available or you want to order from Amazon instead of AliExpress. DO NOT ORDER FROM ALL LINKS or you will wind up with a lot of extra parts you don't need. For most parts, only one or two is needed. Sometimes, buying in higher quantities is actually cheaper than buying a single part. However, since you will need 8 driver modules it makes sense to shop around for the best price. The cheapest I have found was Aliexpress.</p><p><b>Ordering tools and consumables:</b> If you are already an electronics hobbyist, odds are VERY good you will not need any extra tools or supplies. Assuming you don't have the needed tools, links are provided for tools required to complete this project, as well as tools that likely will not be needed but could be helpful.</p><p><b>Soldering Iron</b> - I STRONGLY recommend a soldering iron with an adjustable temperature. Keeping the temperature right is very important to adequate soldering. Aliexpress has them as low as $5.00</p><p><b>Soldering iron holder</b> - You will be picking up and putting down the soldering iron a lot. It might be helpful to have a safe and convenient place to put or lay your soldering iron.</p><p><b>Soldering iron tip cleaner</b> - The soldering iron can get crud on the tip and will need to be cleaned from time to time. Often, you will have too much solder on the tip and need to remove solder. Some soldering irons come with a dry, flat sponge. This is a tip cleaner. Get it wet. Wipe the hot tip over the damp sponge to clean the tip. Do it fast, this isn't meant to burn the sponge. There are also other tip cleaners that work without water. These work as well. If you're trying to do this cheap and don't have a tip cleaner, a wet paper towel can work. Again, wipe fast, don't cook the paper towel.</p><p><b>Solder</b> - There are two main varieties of solder - Lead-free and lead. Lead solder, actually a 60-40 mixture of lead and tin, has been used for decades and works very well. If you don't eat it or fail to wash your hands after use, it's perfectly safe and strongly recommended. Lead-free solder melts at a higher temperature and usually doesn't flow well, making it's use more difficult. Do NOT use solder meant for plumbing! This solder has an acid core and will make a mess for this purpose. In general, higher quality (More expensive) solder flows better and is easier to work with.</p><p><b>Solder wick or desoldering pump</b> - These remove solder. Sometimes, you might find you have too much solder at a point. It might even bridge two or more points, which is very bad. In this case, a way to remove solder is helpful. A solder pump literally sucks up the molten solder. Solder wick or braid will more gently and slowly pull the solder out of a solder conection.</p><p><b>Flux</b> - Flux is literally a magic powder or cream that makes soldering work really well. Without flux, the solder can get chunky and sticky, connecting across multiple pins and causing problems. Adding flux encourages the solder go where it's supposed to, yet it tends to not go where it's not supposed to. Solder actually comes with flux embedded in it's core. This is usually enough flux. You can purchase extra flux separately, and it may be useful.</p><p><b>Alcohol</b> - Especially if you use extra flux, Alcohol is great for cleaning flux off a PCB. With the exception of the LCD, rotary encoder and the speaker (Unless if the tab is still over the hole), all parts are safe to be sprayed, wiped, or even immersed in alcohol. Cleaning the board is probably not necessary but can make a neater finished product, as well as letting you examine connections for proper solder connections.</p><p><b>Magnification</b> - This can be as simple as reading glasses, or more complicated with a magnifier with a built-in light. If you're young with good eyesight, you might not need any magnification at all. It's still good to have.</p><p><b>Files</b> - A file is not required, but very useful for smoothing edges and rounding corners.</p><p><b>Multimeter</b> - While you won't need a multimeter to make a FreedomWavePD, you might need one if your project doesn't work after being finished. A multimeter can let you see what's going on in a way your eyes could never see. You can't tell if current is flowing or what the voltage is at a certain point just by looking. A multimeter lets you see what's going on. A Multimeter is also handy for verifying resistor values.</p>
</body></html>

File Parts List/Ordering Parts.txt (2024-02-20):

Ordering parts:
This project was made with a bit of versatility and flexibility in mind. When you build this board properly, you will see a lot of missing components on the Printed Circuit Board. THIS IS NORMAL. Some parts are for future expansion, experimentation, or just in case there are issues with your particular parts. Follow the instructions and the video and you should end up with a working device.

Ordering a kit:
If you have never soldered or assembled an electronic kit before. I highly recommend you try a kit first. It will be good practice and give you confidence. There are a number of links to kits at Aliexpress.

Ordering the PCB:
The Printed Circuit Board, or PCB, will be ordered from a company that specializes in manufacturing PCB's. The process consists of sending then the FreedomWavePD Gerber files. While you can have any PCB company make your PCB, we have a link at JLCPCB.com and OSHPark.com to make ordering very easy. Simply click on the link, fill in your address and payment info and everything else is all set for you. JLCPCB Requires purchasing 5 boards. As odd as this sounds, purchasing 5 boards from JLCPCB is likely the cheapest way to get a single board. You can make more than one or share the extra boards with others.

Ordering the electronic components:
While there may be other sources, including Ebay, the two sources I decided on are Amazon and Aliexpress. Amazon will usually be much more expensive but you'll probably get the parts faster. Aliexpress has all the parts needed, at often a much lower price. Also, combining shipping or meeting certain minimums may result in shipping discounts. Unfortunately, a part with a similar description may not work with the FreedomWavePD. I have provided links to all parts. They have not all been tested but are believed to work. There are multiple links for each part in case one is not available or you want to order from Amazon instead of AliExpress. DO NOT ORDER FROM ALL LINKS or you will wind up with a lot of extra parts you don't need. For most parts, only one or two is needed. Sometimes, buying in higher quantities is actually cheaper than buying a single part. However, since you will need 8 driver modules it makes sense to shop around for the best price. The cheapest I have found was Aliexpress.

Ordering tools and consumables:
If you are already an electronics hobbyist, odds are VERY good you will not need any extra tools or supplies. Assuming you don't have the needed tools, links are provided for tools required to complete this project, as well as tools that likely will not be needed but could be helpful.

 Soldering Iron - I STRONGLY recommend a soldering iron with an adjustable temperature. Keeping the temperature right is very important to adequate soldering. Aliexpress has them as low as $5.00
 
 Soldering iron holder - You will be picking up and putting down the soldering iron a lot. It might be helpful to have a safe and convenient place to put or lay your soldering iron.
 
 Soldering iron tip cleaner - The soldering iron can get crud on the tip and will need to be cleaned from time to time. Often, you will have too much solder on the tip and need to remove solder. Some soldering irons come with a dry, flat sponge. This is a tip cleaner. Get it wet. Wipe the hot tip over the damp sponge to clean the tip. Do it fast, this isn't meant to burn the sponge. There are also other tip cleaners that work without water. These work as well. If you're trying to do this cheap and don't have a tip cleaner, a wet paper towel can work. Again, wipe fast, don't cook the paper towel.
 
 Solder - There are two main varieties of solder - Lead-free and lead. Lead solder, actually a 60-40 mixture of lead and tin, has been used for decades and works very well. If you don't eat it or fail to wash your hands after use, it's perfectly safe and strongly recommended. Lead-free solder melts at a higher temperature and usually doesn't flow well, making it's use more difficult. Do NOT use solder meant for plumbing! This solder has an acid core and will make a mess for this purpose. In general, higher quality (More expensive) solder flows better and is easier to work with.
 
 Solder wick or desoldering pump - These remove solder. Sometimes, you might find you have too much solder at a point. It might even bridge two or more points, which is very bad. In this case, a way to remove solder is helpful. A solder pump literally sucks up the molten solder. Solder wick or braid will more gently and slowly pull the solder out of a solder conection. 
 
 Flux - Flux is literally a magic powder or cream that makes soldering work really well. Without flux, the solder can get chunky and sticky, connecting across multiple pins and causing problems. Solder actually comes with flux embedded in it's core. This is usually enough flux. You can purchase extra flux separately, and it may be useful.
 
 Alcohol - Especially if you use extra flux, Alcohol is great for cleaning flux off a PCB. With the exception of the LCD and the speaker (Unless if the tab is still over the hole), all parts are safe to be sprayed, wiped, or even immersed in alcohol. Cleaning the board is probably not necessary but can make a neater finished product, as well as letting you examine connections for proper solder connections.
 
 Magnification - This can be as simple as reading glasses, or more complicated with a magnifier with a built-in light. If you're young with good eyesight, you might not need any magnification at all. It's still good to have.
 
 Files - A file is not required, but very useful for smoothing edges and rounding corners.
 
 Multimeter - While you won't need a multimeter to make a FreedomWavePD, you might need one if your project doesn't work after being finished. A multimeter can let you see what's going on in a way your eyes could never see. You can't tell if current is flowing or what the voltage is at a certain point just by looking. A multimeter lets you see what's going on. A Multimeter is also handy for verifying resistor values.

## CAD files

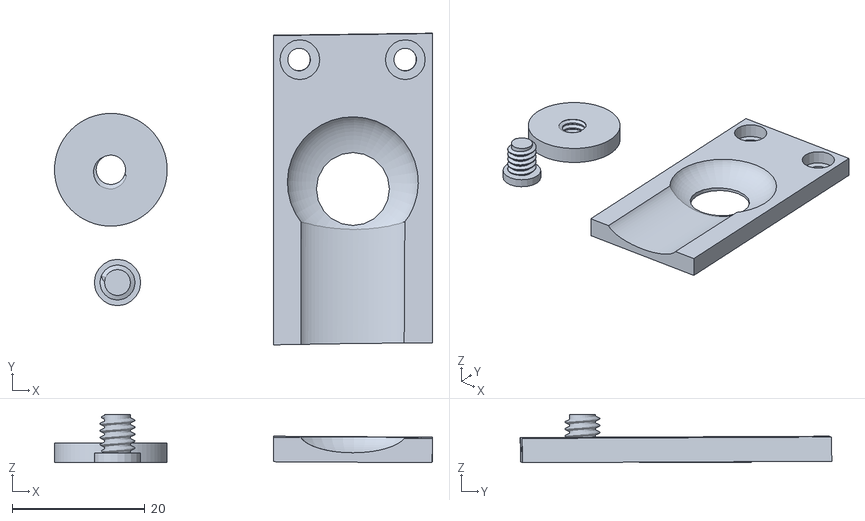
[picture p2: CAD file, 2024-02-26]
Gloves/Parkgloveman DAEX 13 Mounting/top plate set.stl
57.0 x 47.0 x 7.30

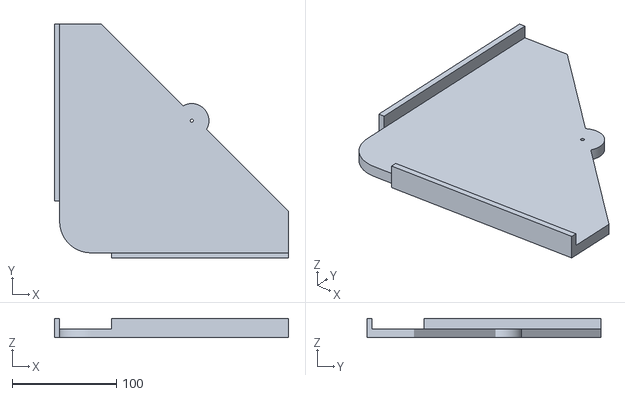
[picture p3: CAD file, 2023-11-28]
Hardware/Corner_Jig/RoundedCornerJig-FreedomWave.stl
225.0 x 225.0 x 18.5

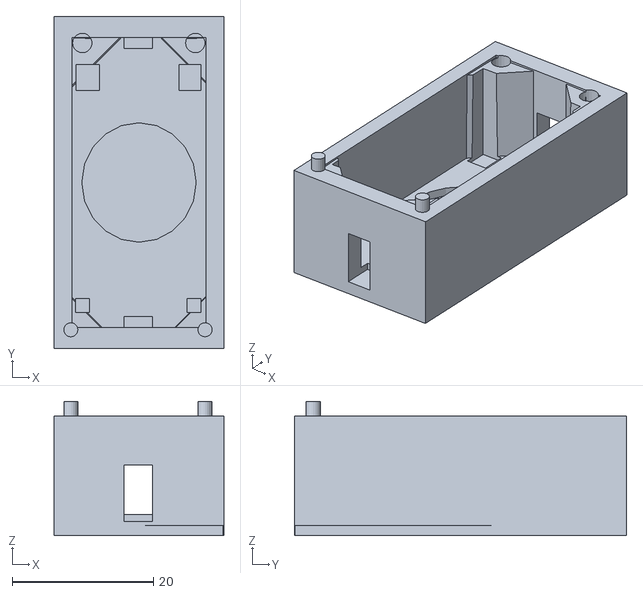
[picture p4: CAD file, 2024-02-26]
Gloves/Parkgloveman DAEX 13 Mounting/grooved box.stl
24.0 x 47.0 x 19.0

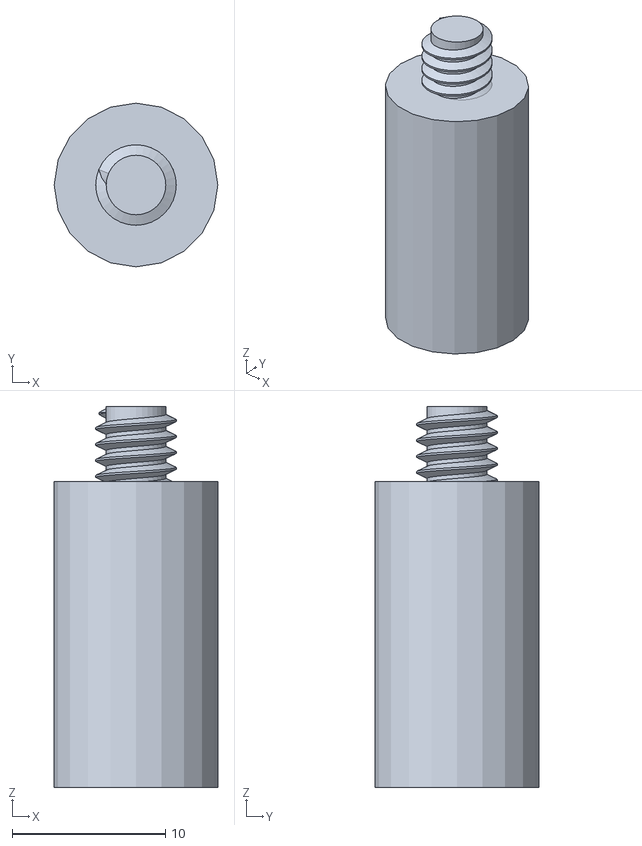
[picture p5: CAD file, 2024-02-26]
Gloves/Parkgloveman DAEX 13 Mounting/mounting jig.stl
10.7 x 10.7 x 24.9

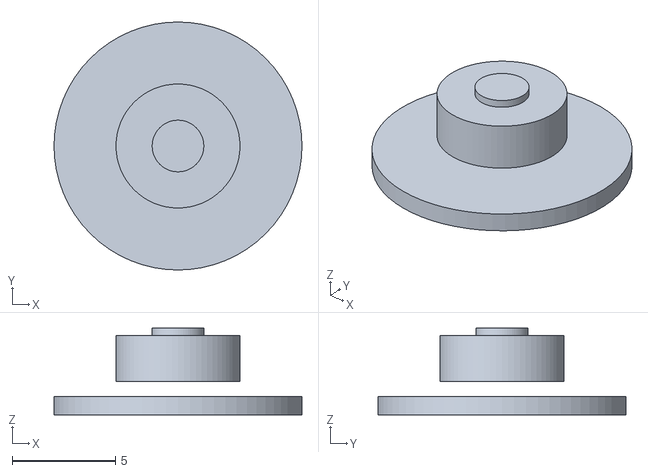
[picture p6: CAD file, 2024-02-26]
Gloves/Parkgloveman DAEX 13 Mounting/Mk5 contact.stl
12.0 x 12.0 x 4.20

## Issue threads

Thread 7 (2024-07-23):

### ISSUE TITLE
Compiled Hex File for v.0.9.8

### ISSUE THREAD

**Issue by kreefd** [RChadwick7/FreedomWavePD#7]
Hi,

i was again reading all necessary steps as i am waiting for parts arriving.
Might it be possible to upload the already compiled file for v0.9.8. ?

Thanks in advance

Kind Regards

kreefd

**Comment by RChadwick7** [comment]
If you already have the Arduino Nano, you absolutely can flash the firmware without the rest of it, but it might be hard to test that everything went OK. In general, if the flash software doesn't give an error message and you see the bar graph display while flashing, it should be good.

**Comment by kreefd** [comment]
Oh okay, thank you. It was a mistake anyway of me.
I was cloning this repo:
https://github.com/RChadwick7/FreedomWavePD.git

 as i thought thats all the files needed.


And now i saw when i click on the right side of the Mainpage on Releases 0.9.8
That i can there download the .zip which includes the other files:

This link:
https://github.com/RChadwick7/FreedomWavePD/releases/download/v0.9.8/FreedomWavePD-0.9.8.zip

**Comment by kreefd** [comment]
C:\Users\kreefd\Desktop\gloves\FreedomWavePD\Software\v0.9.8>avrdude -C avrdude.conf -v -patmega328p -carduino -p4 -b57600 -D -Uflash:w:FreedomWavePD-0.9.8.hex:i

avrdude: Version 7.2
         Copyright the AVRDUDE authors;
         see https://github.com/avrdudes/avrdude/blob/main/AUTHORS

         System wide configuration file is C:\Users\kreefd\Desktop\gloves\FreedomWavePD\Software\v0.9.8\avrdude.conf

         Using Port                    : com4
         Using Programmer              : arduino
         Overriding Baud Rate          : 57600

avrdude part_not_found() error: AVR part 4 not found

Valid parts are:
  uc3a0512   = AT32UC3A0512       [C:\Users\kreefd\Desktop\gloves\FreedomWavePD\Software\v0.9.8\avrdude.conf:17536]
    - AT32UC3A0512-ALTR:    LQFP144,  Fmax=66 MHz, T=[-40 C, 85 C], Vcc=[1.65 V, 3.6 V]
    - AT32UC3A0512-ALTRA:   LQFP144,  Fmax=66 MHz, T=[-40 C, 85 C], Vcc=[1.65 V, 3.6 V]
    - AT32UC3A0512-ALTT:    LQFP144,  Fmax=66 MHz, T=[-40 C, 85 C], Vcc=[1.65 V, 3.6 V]
    - AT32UC3A0512-ALTTA:   LQFP144,  Fmax=66 MHz, T=[-40 C, 85 C], Vcc=[1.65 V, 3.6 V]
    - AT32UC3A0512-ALUR:    LQFP144,  Fmax=66 MHz, T=[-40 C, 85 C], Vcc=[1.65 V, 3.6 V]
    - AT32UC3A0512-ALUT:    LQFP144,  Fmax=66 MHz, T=[-40 C, 85 C], Vcc=[1.65 V, 3.6 V]
    - AT32UC3A0512-CTUR:    TFBGA144, Fmax=66 MHz, T=[-40 C, 85 C], Vcc=[1.65 V, 3.6 V]
    - AT32UC3A0512-CTUT:    TFBGA144, Fmax=66 MHz, T=[-40 C, 85 C], Vcc=[1.65 V, 3.6 V]
    - AT32UC3A0512AU-ALTRA: LQFP144,  Fmax=66 MHz, T=[-40 C, 85 C], Vcc=[1.65 V, 3.6 V]
    - AT32UC3A0512AU-ALUT:  LQFP144,  Fmax=66 MHz, T=[-40 C, 85 C], Vcc=[1.65 V, 3.6 V]
  89S51      = AT89S51            [C:\Users\kreefd\Desktop\gloves\FreedomWavePD\Software\v0.9.8\avrdude.conf:2954]
  
  
  One of the first lines says:
  
  avrdude part_not_found() error: AVR part 4 not found
  
  but there seems configurations taken place afterwards and no more errors occur.

**Comment by RChadwick7** [comment]
It's probably good, as long as you saw the bargraph go across as it was programming. Some Arduinos use 57600baud and others 115kbaud. The install script tries one, then the other. If the first one isn't the right baud rate, you'll see an error. As long as one works, you're good.

**Comment by kreefd** [comment]
Unfortunately i don't see a bar graph in the terminal. 
Yes i had to use the 57600 baud that gives the response above with the 
first line : 

avrdude part_not_found() error: AVR part 4 not found

I forgot to mention i had to change the default serial port in the **avrdude.conf**

`default_serial     = "com1";`
 to
`default_serial     = "com4";`

as my device manager shows **com4** for the arduino .


Also i had to change the line :
`avrdude -C avrdude.conf -v -patmega328p -carduino **-P4** -b57600 -D -Uflash:w:FreedomWavePD-0.9.8.hex:i`

**to**

`avrdude -C avrdude.conf -v -patmega328p -carduino **-p4** -b57600 -D -Uflash:w:FreedomWavePD-0.9.8.hex:i`

small **-p** instead of **-P**.

I dont know why but with **-P4** it says :

```
C:\Users\kreefd\Desktop\gloves\FreedomWavePD\Software\FreedomWavePD-0.9.8>avrdude -C avrdude.conf -v -patmega328p -carduino -P4 -b57600 -D -Uflash:w:FreedomWavePD-0.9.8.hex:i


avrdude: Version 7.2
         Copyright the AVRDUDE authors;
         see https://github.com/avrdudes/avrdude/blob/main/AUTHORS

         System wide configuration file is C:\Users\kreefd\Desktop\gloves\FreedomWavePD\Software\FreedomWavePD-0.9.8\avrdude.conf

         Using Port                    : 4
         Using Programmer              : arduino
         Overriding Baud Rate          : 57600
avrdude ser_open() error: cannot open port 4: Das System kann die angegebene Datei nicht finden.

avrdude main() error: unable to open programmer arduino on port 4


avrdude done.  Thank you.
```

I have now soldered everything except the DRV2605 as i am waiting for arrival.
Would it be possible to see already something on the screen , expected that the arduino was flashed correctly ?

Thank in you advance

Kind Regards
Kreefd

**Comment by kreefd** [comment]
Great News ,
 can't believe it was the syntax of the command.

avrdude -C avrdude.conf -v -patmega328p -carduino **-P COM4** -b 57600 -D -U flash:w:FreedomWavePD-0.9.8.hex:i

so when i use **-P COM4** and not -P4 or -p4 it works. i can see the FreedomWavePD Ver.0.9.9 *6731* on the display now and can scroll the menu with the controller.

**Comment by RChadwick7** [comment]
I'm glad you figured out the syntax. I'll put it on my to-do list to make it more clear.

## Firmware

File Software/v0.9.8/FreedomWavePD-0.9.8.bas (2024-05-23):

   '
   '  **********************************
   '  *  Parkinson's Gloves Ver 0.9.8  *
   '  *         FreedomWavePD          *
   '  *   (c) 2023 Charles Bailey      *
   '  *  Compiled with Bascom 2.0.8.6  *
   '  **********************************
   '
' ATMega328 has 3 timers. 0 and 2 are 8 bit, 1 is 16 bit. Fingers use Timer1.

' Fingers are arranged this way:
'    Left Hand       Right Hand
'      0  1  2  3  4  5  6  7

' 0 is left pinky
' 1 is left ring
' 2 is left middle
' 3 is left index
' 4 is right index
' 5 is right middle
' 6 is right ring
' 7 is right pinky
'
' 8 is left thumb
' 9 is right thumb

$programmer = 22                                            'ARDUINO (using stk500v1 protocol)
$regfile = "m328pdef.dat"                                   'Set the AVR to use - ATMega328.
$crystal = 16000000                                         'Set the AVR clock.
   '
$hwstack = 120                                               'Set the capacity of the hardware stack.
$swstack = 120                                               'Set the capacity of the software stack.
$framesize = 180                                             'Set the capacity of the frame area.

Config RND = 32

UCSR0B = 0 ' Disables the serial port, left enabled by some bootloaders



'###############################################################################
'##             V A R I A B L E S  T O  S A V E  T O  E E P R O M             ##
'###############################################################################



'
 Dim AutoStart as Byte      'Not a mistake, bit values have to be bytes in the menu system
 Dim Treatment_time as Byte
 Dim Vib_Intensity as Byte
 Dim JitterSetting as Word
 Dim HandMirror as Byte     'Not a mistake, bit values have to be bytes in the menu system.
 Dim ERM_LRA_Setting as String * 3
 Dim OL_CL_Setting as String * 6
 Dim Drive_Voltage as Single
 Dim LRA_OPEN_LOOP  as Byte 'Not a mistake, bit values have to be bytes in the menu system
 Dim ERM_OPEN_LOOP as Byte  'Not a mistake, bit values have to be bytes in the menu system

 Dim Is_LRA as Byte         'Not a mistake, bit values have to be bytes in the menu system
 Dim Is_OL as Byte          'Not a mistake, bit values have to be bytes in the menu system

' Dim Temp_Voltage as Single
 ' ------------------------------------------------------------------------------------------------


'###############################################################################
'##                    D I M E N S I O N  V A R I A B L E S                   ##
'###############################################################################

'Config Minute/Hour timer
'Each period of 166.66ms x 36 = 1 minute, almost exactly

 Dim PeriodCount as Byte
 Dim MinuteTimer as Byte
 Dim SWVer as String *  5
 Dim ReadRegister as Byte

Config PortD = output  ' Set PortD for fingers output

' This turns off the output so the Init routine vibrations will stop when done.
PORTD = &H00

 Dim ___rseed as word

'Config Timing Variables
 Dim PulseStart As Word
 Dim PulseLength As Word
 Dim PulseStarting as bit
 Dim PeriodLength as Word
 Dim FirstHand as Byte
 Dim SecondHand as Byte
 Dim OnCount as Byte  ' The number of cycles the 4 finger pattern repeats. Standard is 3
 Dim OffCount as Byte ' The number of cycles of 4 finger patterns to rest. Standard is 2
 Dim MaxOn as Byte
 Dim MaxOff as Byte
 Dim LastFinger as Byte

' Jitter is +/- 20ms. 40ms total.0 to 624! This is used in timing loop..
 Dim PulseStartWJitter as Word

'Config Random Variables
 Dim ArrayLength as Byte
 Dim ArrayLengthPlusOne as Byte
 Dim i as Byte
 Dim j as Byte
 Dim Finger(8) as Byte
 Dim holdi as Byte
 Dim Holdj as byte

 Dim NeedRandom as Bit
 Dim FingerCount as Byte

 Dim LoopArray as Byte

 Dim i2cvalue1 as Byte
 Dim i2cvalue2 as Byte
 Dim i2cvalue3 as Byte

 Dim ChipType as String * 8
 Dim AdcVal As Word         ' This is to detect the Autostart jumper
 Dim TreatmentActive as Bit ' If this is a 1, then we are actively doing treatment, or should be

 Dim LRA_Frequency as Word
 Dim RATED_VOLTAGE as Byte
 Dim OD_CLAMP as Byte
 Dim OL_LRA_PERIOD as Byte       ' Make this a single?
 Dim Temp2 as Single
 Dim Temp3 as Single


 Dim Old_Is_LRA as Byte
 Dim Old_Is_OL  As Byte
 Dim Old_Vib_Intensity as Byte
 Dim Old_Drive_Voltage as Single
 Dim Old_LRA_Frequency as Word


 Dim SAMPLE_TIME as Word


 Dim Menu_value_active_old As Bit ' Used by menu system to determine when menu changed something

'###############################################################################
'##                   S E T  V A R I O U S   V A R I A B L E S                ##
'###############################################################################

' ------------------
   SWVer = "0.9.8"        '< UPDATE THIS WITH EACH VERSION
' ------------------

FingerCount = 1
Sample_Time = 300

MaxOn = 3 * 8' It's multiplied by two as this gets run at starting AND stopping pulse
MaxOff = 2 * 3 ' Same reason. This works, not sure why (Remember 66ms!!)
MaxOff = MaxOff + 1 ' This makes timing right for the off period
OnCount = 0
OffCount = 0

PulseStart = 35  ' Start of pulse. Jitter is only ADDED to this, so not critical.
PulseLength = 1562 ' This is 100ms (1526)
PeriodLength = 2604 ' This is 166.6ms (2604) (Multiply ms by 15.624 to get time value.
PulseStarting = 1

ArrayLength = 4  ' 0 to 3                This determines if we are doing 4 fingers mirrored or 8 fingers
ArrayLengthPlusOne = ArrayLength + 1

'NeedRandom = 1   ' Logically it should be here, but output different, not necessarily better.

Config PortD = output  ' Set PortD for fingers output

' We set the initial array numbers:
        Finger(1) = 0
        Finger(2) = 1
        Finger(3) = 2
        Finger(4) = 3
        Finger(5) = 4
        Finger(6) = 5
        Finger(7) = 6
        Finger(8) = 7

'###############################################################################
'##           C O N F I G U R E   R O T A R Y   E N C O D E R                 ##
'###############################################################################

Encoder_switch Alias PinC.2
Dim B As Byte
Dim Encoder_switch_old As Bit
Dim Encoder_turn_left As Byte , Encoder_turn_right As Byte
PortC.0 = 1                                              ' pullup encoder a,
PortC.1 = 1                                              ' pullup encoder b,
PortC.2 = 1                                              ' pullup encoder switch
Dim skip_flagL as byte    ' This is used for this specific encoder. Otherwise, one notch registers as two!
Dim skip_flagR as byte    ' This is used for this specific encoder. Otherwise, one notch registers as two!


'###############################################################################
'##                C O N F I G U R E   M E N U   T I M E R                    ##
'###############################################################################

Const Ticker_hwtimer = 2                                    ' Choose which hardware timer to use
Const Ticker_frequency = 1000                               ' set the timer resolution
Const Tickers = 2                                           ' # of software timers to use
$include "tickers.inc"
Const Timer_readswitches = 1
Const Timer_valueupdate = 2


'###############################################################################
'##                       C O N F I G U R E   L C D                           ##
'###############################################################################

$lib "i2c_twi.lib"                                       'Incorporate the hardware I2C/TWI library.
Config Twi = 100000                                      'I2C bus clock = 100KHz
Config Scl = Portc.5                                     'You must specify the SCL pin name.
Config Sda = Portc.4                                     'You must specify the SDA pin name.
I2cinit                                                  'Initialize the SCL and SDA lines of the I2C bus.
Reset Watchdog
Dim Pcf8574_lcd As Byte : Pcf8574_lcd = &H4E             'PCF8574 slave address. (&H40,&H42,&H44,&H46,&H48,&H4A,&H4C,&H4E)
Dim Backlight As Byte : Backlight = 1                    'LCD backlight control. (0: off, 1: on)
$lib "lcd_i2c_PCF8574.LIB"                               'Incorporate the library of I2C LCD PCF8574 Adapter.
Config Lcd = 16x2                                        'Set the LCD to 16 characters and 2 lines.
Initlcd                                                  'Initialize the LCD.


'###############################################################################
'##                     C R E A T E   R A N D O M   S E E D                   ##
'###############################################################################

CONFIG ADC = Single, PRESCALER = Auto,  REFERENCE = Avcc

Reset Watchdog

Dim Adc_word as word
Dim Bit_num as Byte
Dim Rnd_word as word

For I = 1 To 72
Reset Watchdog
   For Bit_num = 0 To 7
      Start ADC
      Adc_word = Getadc(Bit_num)
      Stop ADC
      Rotate Rnd_word , Left
      Rnd_word = Rnd_word Xor Adc_word
   Next
Next


___rseed = Rnd_word


'###############################################################################
'##                     C O N F I G U R E  T I M E R S                        ##
'###############################################################################

Compare1B = PulseStart       ' The first time we don't bother with jitter
Compare1A = PeriodLength

Config Timer1 = Timer , Prescale = 1024  , Clear_timer = 1
On Compare1B StartPulse

Enable Compare1a
Enable Compare1b
Enable Interrupts
Stop Timer1
Reset Watchdog


'###############################################################################
'##                    C O N F I G U R E  W A T C H D O G                     ##
'###############################################################################

CONFIG WATCHDOG = 2048

Start Watchdog
Reset Watchdog


'###############################################################################
'##      L C D   M E N U                                                      ##
'###############################################################################

Macro Menu_include_data

' include the data file created with the menu designer
 $Include "PARKINSONS_menu_data4.inc"
End Macro

'Include just the Menu.inc
$include "menu.inc"

'###############################################################################
'##    M E N U    V A R I A B L E S                                           ##
'###############################################################################

Dim Test_string As String * Menu_value_string_width         ' max string length is stored in a constant
Dim Tempbyte As Byte


'###############################################################################
'##      M E N U   I N I T                                                    ##
'###############################################################################

Encoder_switch_old = Encoder_switch

Ticker_time(timer_readswitches) = 20                        ' 20 ms debounce
Ticker_enabled(timer_readswitches) = True
Ticker_time(timer_valueupdate) = 500                        ' 500 ms read-only value update
Ticker_enabled(timer_valueupdate) = True

Menu_init


'###############################################################################
'##                  Run System Self Check of All Devices                     ##
'###############################################################################

 Gosub TestSystem


'###############################################################################
'##  P R O G R A M   C H I P S   F R O M   S A V E D   M E N U   V A L U E S  ##
'###############################################################################

 Gosub NewSetupChips
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

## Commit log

2023-11-29 Moved into Hardware folder
    [RoundedCornerJig-FreedomWave.stl]
2023-12-09 Defective PCB Design
    There were some issues with the PCB design.
2024-02-21 Update README.md
    Added link to the assembly video
2024-02-26 Added info on Gloves
    [Mk5 contact.stl, grooved box.stl, mounting jig.stl, top plate set.stl]
